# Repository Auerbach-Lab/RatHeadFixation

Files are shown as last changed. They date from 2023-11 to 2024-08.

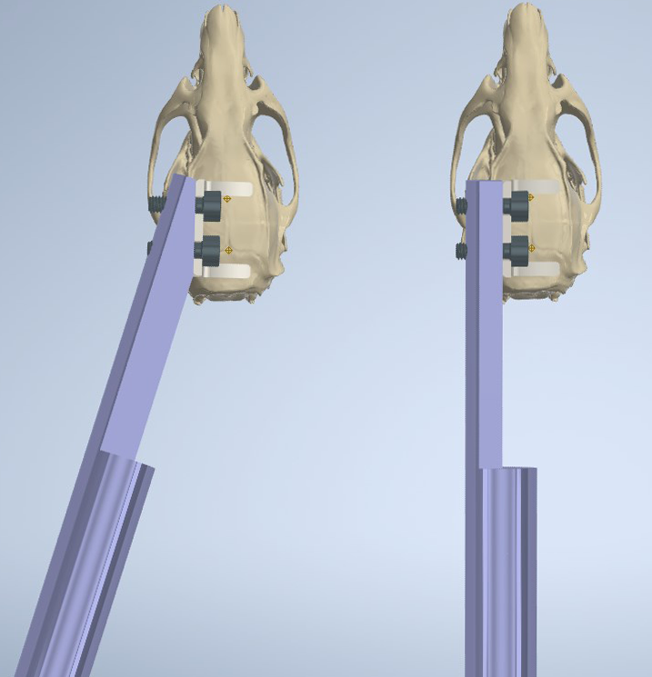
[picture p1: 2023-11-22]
Hight Adaptation/usage_headbars.png

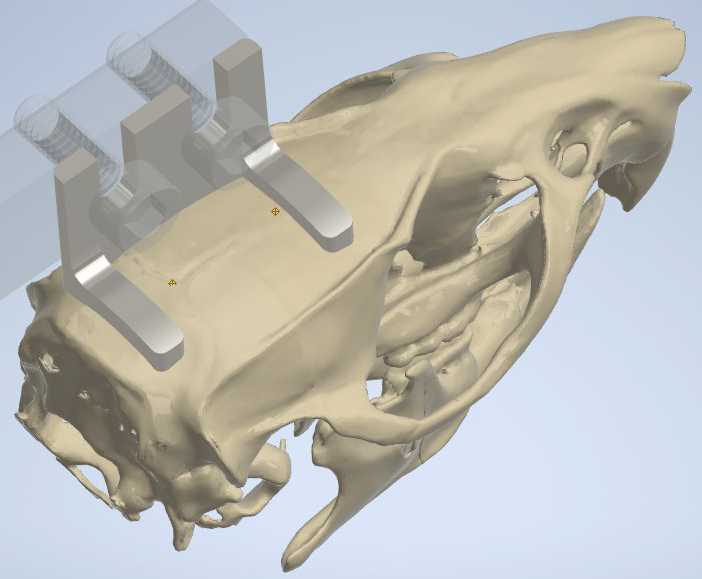
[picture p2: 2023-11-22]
Hight Adaptation/usage_ax_v03.png

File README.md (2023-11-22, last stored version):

# Rat Head Fixation System

 - **Author:** Brian James, \<james29@illinois.edu>
 - **Date:** 2022-08-20
 - **Version:** 0.3.5
 - **Primary Investigator:** Ben Auerbach, Auerbach Lab, University of Illinois \<bda5@illinois.edu>

## Description
This is a head fixation system for adult laboratory rats, suitable for audiology research. It is derived from the Hight mouse head fixation system. Headplates were re-created using the Hight plates as guidance, but in larger dimensions and contoured to match a CT scan of a rat skull. The mounting hole spacing was widened to minimize torque, and the mating portion of the angled headbar was thickened for additional strength. Because of the different mounting hole spacing, the two systems do not share interchangable parts.

## Parts
**rat_headplateACx** -- The primary headplate design, compatible with straight or angled headbar. This design is symmetrical; it can be used with the mounting plate on the left or the right side interchangably. Headplates can be 3d printed in stainless steel (such as 316) from a variety of manufacturers; [Craftcloud](craftcloud3d.com) allows easy comparison shopping. 

**rat_headplateIC** -- Alternative headplate suitable for probing the inferior colliculus or other regions requiring a dorsal approach. This design is compatible with straight headbar only. While it will mate with the angled headbar, the bar would need to pass downward through the bench top when securing a prone rat. This design is necessarily asymmetrical but can be mirrored for use with a right side headbar. This design is still version 0.1.

**rat_headbarStraight** -- Simple rod to which the plate is secured while in use, machined from 0.5" diameter rod stock, e.g. [Grainger #3ANN6](https://www.grainger.com/product/GRAINGER-APPROVED-Rod-Stock-316-3ANN6). Stainless steel alloy 316 is recommended for its improved resistance to corrosion, particularly if using cleaning solutions that decompose to produce chloride ions, such as bleach or benzalkonium chloride (Lysol, Microban, 3M Quat, most disinfecting wipes, etc).

**rat_headbarAngled** -- An alternative headbar design which may be useful if positioning the rat on a floating ball or similar movable surfaces.

**#5-40 Socket Head Cap Screw, 3/8 Length, 3/32 Hex"** -- Two screws are required per head**bar** for fastening a headplate, e.g. [Grainger #6XA50](https://www.grainger.com/product/GRAINGER-APPROVED-Socket-Head-Cap-Screw-5-40-6XA50).

**3/32 Hex Key / Allen Wrench** -- Socket head screws are driven using a hex key, e.g. [Grainger #38TG47](https://www.grainger.com/product/EKLIND-Hex-Key-3-32-in-Tip-Size-38TG47), rather than a screwdriver. A ball-end key is more convenient since it can be used at multiple angles. Verify the drive size of the fasteners you're using; #5 screws may require either 5/64" or 3/32" drive.

**C&B Metabond Dental Cement System** -- Only the following components are specifically
required:

 - Etchant Gel (S395)
 - Quick Base (S398)
 - C Universal TBB Catalyst (S371)
 - Radiopaque Tooth Shade Powder (S396)
 - Measuring Scoop (S378)
 - Ceramic Mixing Dish With Temperature Indicator (S387)

The remaining components from the all-in-one kit (S380) -- dentin activator, clear powder, applicator tools and brushes -- are not needed. If purchasing the kit, the clear powder may also be used interchangably with the opaque powder.

**Speedball India Ink** -- Used for dyeing the cement mixture. This brand is specifically
recommended by Hight for its consistency and imparted blackness.

**Toothpicks** and **Cotton/Foam Swabs** -- Used to apply cement and etchant, respectively.

## Files
The master assembly file is `rat_head_fixation_assembly.iam`, which shows how parts fit together and sit on the skull. That assembly and the individual `.ipt` part files are in Autodesk Inventor formats.

Dimensional drawings of the headbars are provided as `.dwg` Autodesk drawings and as PDFs, to be given to a machine shop. Only imperial unit versions are provided since both the base rod stock and the fasteners are in imperial units. Metric users should redefine the headbar to be machined from metric rod stock, probably 12 mm, and change the tapped holes to M3. No dimensional drawings are provided for headplate files, as these are intended to be 3d printed directly from the `.ipt` or `.stl` files. Part `.stl` files are dimensioned in millimeters.

Other provided files include the rat skull model in its original format (`RatSkull_Mesh1.stl`), a cropped version with a reduced vertex count created in Autodesk Meshmixer (`ratskull.mix`), and intermediate `.obj` files and corresponding `.ipt` files for the skull and cutaway profile views. There is also a sample 16x Nikon LWD microscope objective model to test clearance.

All files created for the Rat Head Fixation System have filenames prefixed with `rat` to differentiate them from similar Hight files. Manufacturer-provided files such as fasteners were not renamed.

## Usage
The AX headplate is intended to be positioned just forward of bregma, nearer to bregma
than to lambda, as pictured below. The angled headbar can be used when there needs to be
clearance behind the rat, such as when using a floating ball setup.

  

### Directions
1. Remove the ceramic mixing dish from freezer and place over ice to keep it cold.
2. Thoroughly clean cranium of any remaining tissue/periosteum and moisture.
3. Saturate swab with etchant, then apply swab over cleaned cranium surface. Let stand 30 seconds, then immediately and thoroughly wipe off with a clean swab. Be careful to not let etchant contact any soft tissue.
4. Position and fixate the headplate over the cranium using the headbar.
5. Prepare the cement. With the mixing dish still on ice, add (in this order) to one well: **4-5 drops Quick Base** (immediately re-cap container), **1 drop India Ink**, **1 drop Catalyst**  (immediately re-cap syringe). Mix gently, for no more than 5 seconds. Finally, add **2 scoops Radiopaque Powder** and stir gently for 5-10 seconds to a creamy consistency.
6. Using clean toothpicks, apply cement mixture to bond the cranium and headplate. Once applied to the headplate, the cement quickly solidifies in seconds to minutes.
7. Clean ceramic mixing dish before cement fully cures.
8. Allow the cement to set for 6 minutes (and allow at least 30 minutes before applying force to the headplate). Afterward, leave no part of the cranium exposed to air.

### Notes
 - Store the ceramic mixing dish in the freezer to ensure it is thoroughly chilled before use.
 - For best results, store mixing dish upside down, with water added to fill the base so that the entire dish is in contact with ice for the procedure.
 - Cured cement on instruments or the mixing dish can be softened by soaking in acetone or chloroform.
 - Coating surfaces in KY, petroleum jelly, glycerine, or mineral oil will prevent cement from bonding to them.
- Cement viscosity increases over time after being mixed.
- Working time for the cement mixture is 2 minutes at 15°C, or up to 5 minutes if kept colder. If the mixture is allowed to come to room temperature (24°C) the working time is cut to 20 seconds or less.
- Headplate implantations using this technique have been tested to be functional for at least 3 months.

## Sources
**Hight Mouse Head Fixation System**
Sandra Romero, Ariel E Hight, Kameron K Clayton, Jennifer Resnik, Ross S Williamson, Kenneth E Hancock, Daniel B Polley, Cellular and Widefield Imaging of Sound Frequency Organization in Primary and Higher Order Fields of the Mouse Auditory Cortex, _Cerebral Cortex_, Volume 30, Issue 3, March 2020, Pages 1603–1622, https://doi.org/10.1093/cercor/bhz190

**3D .stl File of Rat Skull**
M. Pohl, Bernd; Fernando Gasca; Olaf Christ; Hofmann, Ulrich G. (2013): 3D .stl file of rat skull. figshare. Dataset. https://doi.org/10.6084/m9.figshare.777745.v1

**3D .stl File of Mouse Skull**
Rowe T, Demarest M. (2001): "Mus musculus". Dataset: Digital Morphology. http://digimorph.org/specimens/Mus_musculus/

**Mouse Skull from Mouse skull (from micro-CT)**
https://www.thingiverse.com/thing:20200 by [MarkU](https://www.thingiverse.com/MarkU)


**16X Nikon CFI LWD Plan Fluorite Objective - CAD files**
https://www.thorlabs.com/thorproduct.cfm?partnumber=N16XLWD-PF

**Socket Head Cap Screw - CAD files**
https://www.grainger.com/product/GRAINGER-APPROVED-Socket-Head-Cap-Screw-5-40-6XA50

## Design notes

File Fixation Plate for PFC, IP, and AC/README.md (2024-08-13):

# Rat Head Fixation System

 - **Author:** Brian James, \<james29@illinois.edu>
 - **Date:** 2024-06-05
 - **Version:** 2.4
 - **Primary Investigator:** Ben Auerbach, Auerbach Lab, University of Illinois \<bda5@illinois.edu>

## Description
This is a novel head fixation system for adult laboratory rats, suitable for audiology research, intended to allow free access to the inferior colliculus, prefrontal cortex, and auditory cortex.

## Files
**Assembly - v4** -- The headplate and fixation aseembly. Headplates can be 3d printed in stainless steel (such as 316) from a variety of manufacturers; [Craftcloud](craftcloud3d.com) allows easy comparison shopping. The leading edge of the headplate sits roughly along the coronal suture when properly positioned on the skull.

## Associated Parts
**Drilling template** -- Cut-down headplate with substantially reduced thickness to facilitate marking locations of screw holes onto the skull. Print in same material (i.e. steel) at same scaling compensation as the main headplate to ensure identical spacing.

**Pigma Micron marker, #01 (0.25mm)** -- This permanent marker fits within the drilling template's holes, allowing precise marks on the skull of the locations for burr holes. The 01 (0.25mm felt tip) size offers the best fit and leaves the largest possible mark. The smaller 005 (**not** 05) and 003 size also fit. Sharpie Ultra-Fine markers do not quite fit. Cover the area to be marked with a thin layer of cyanoacrylate glue (CA, super, krazy, vetbond) to get a dry surface for marking; this procedure is also supposed to increase the bonding strength of MetaBond.

**Button-head torx screws, #0-80 thread, 3/16" long** -- Two bone screws are optionally used per headplate, e.g. [McMaster #90910A667](https://www.mcmaster.com/90910A667/). The headplates are to be tapped with #0-80 threads on the provided holes to mate with the screws. **It is not necessary to completely tighten the screws**; the protrusion beneath the headplate should be carefully judged. The screws are intended for additional security only, as the thickness of the skull only allows approximately 1.5 complete threads embedded in bone, and requires precision on drilled hole diameter on the order of 50 microns to avoid easily pulling free. **C&B MetaBond should be used as the primary affixative** of the headplate. 

**Torx-plus bit (size IP5) & driver** -- Socket head screws are driven using a torx+ bit, e.g. [McMaster #54305A18](https://www.mcmaster.com/54305A18/). A mini ratcheting 1/4" shank driver e.g. [McMaster #52815A22](https://www.mcmaster.com/52815A22/) is appropriate for these bits. Torx-plus was chosen for its superior torque application given the extremely small size of the screws, and for its ability to easily 'grab' a screw simply by mating.

**Spiral or burr drill bit, 1.2mm diameter** -- #0 (1.52mm) screws mate with a 75% thread hole of 1.19mm, used for soft metals (brass, aluminum) and plastics, or with a 50% thread hole of 1.32mm for hard metals (iron, steel). The smaller the burr hole, the more bite you will have, but the more resistance you will encounter setting the screw, since the bone is not tapped. Since only 1-2 threads will interface with the bone, however, the lab's existing 1.2mm burr bit should be fine.

**Standoffs, 1/4"-20 thread, various lengths** -- A variety lengths of [standoffs](https://www.mcmaster.com/products/male-female-threaded-hex-standoffs/male-female-threaded-hex-standoffs-6/thread-size~1-4-20/material~stainless-steel-2/material~18-8-stainless-steel/), all of which can mate with the ThorLabs table and each other. These provide the clamping surface used with either end of the headplate. Extra standoffs allow use in combination to assemble a clamping surface at any desired height above the bed of the table.

**Threaded inserts, #6-32 to 1/4"-20** -- 
Threaded inserts [McMaster #90247A008](https://www.mcmaster.com/90247A008) are installed in the shortest pair of standoffs. Consider adding the remaining pair of inserts to the single most appropriate length of standoff as well. The inserts allow mating with the cam clamps that top the standoffs in use. Installation of threaded inserts is permanent. 

**Clamping handle with threaded stud, #6-32 thread, 3/8" long**  -- These clamps, e.g. [McMaster #5720K25](https://www.mcmaster.com/5720K25/) are fastened to the top standoffs in use, with the aid of the threaded inserts. They should be threaded into the standoff so that the plate can be quickly inserted onto the exposed threaded stud, so sandwiched between the circular plastic piece above and the standoff's surface below. Operating a clamp can be done one-handed in approximately a single second. When engaged, clamps exert up to 1400 N of clamping force.

## Assembly
Partial assembly, showing interactions of pieces in use
Partial assembly, showing relationships of pieces in use: two stacked standoffs, cam clamp, bone screw, and headplate. Yellow crosshairs indicate probe locations for PFC, IC, and AC. **Note the position of the headplate relative to the corornal suture.** The headplate fits standoffs positioned exactly 2" apart; the hole spacing on the ThorLabs air table is 1", so there will be one empty hole between the two locations where standoffs are inserted.
<br><br><br>

Partial assembly, showing position of lab rat Above, with position of lab rat visualized. A shorter standoff (not pictured) may be used in the center position between the standoffs used for clamps, to support the animal's jaw and head.
<br><br><br>

Using 3/16" screws, up to 6 full threads (~1.9mm) will protrude beneath the headplate. Before mixing the metabond, the surgeon should thread the screws to the desired depth, then back the screws until they are flush with the headplate's lower surface while counting the revolutions made. During the surgery, retighten the screws by the same number of revolutions to drive them to the predetermined depth.

**It is not necessary to tighten the head of the screw to sit flush against the headplate.** Doing so only adds one additional threading to the ~7 threads already engaged within the body of the headplate.

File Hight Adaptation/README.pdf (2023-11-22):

# Rat Head Fixatition System

Author: Brian James
Date: 2022-08-20
Version: 0.3.5
Contact: Ben Auerbach, Auerbach Lab, University of Illinois <bda5@illinois.edu>

## Descriptition

This is a head fifixatition system for adult laboratory rats, suitable for audiology research. It is derived from the Hight mouse head fifixatition system. Headplates were re-created using the Hight plates as guidance, but in larger dimensions and contoured to match a CT scan of a rat skull. The mountiting hole spacing was widened to minimize torque, and the matiting portition of the angled headbar was thickened for addititional strength. Because of the difffferent mountiting hole spacing, the two systems do not share interchangable parts.

## Parts

rat_headplateACx – The primary headplate design, compatitible with straight or angled headbar. This design is symmetrical; it can be used with the mountiting plate on the leftft or the right side interchangably. Headplates can be 3d printed in stainless steel (such as 316) from a variety of manufacturers; Craftftcloud (https://stackedit.io/craftcloud3d.com) allows easy comparison shopping.

rat_headplateIC – Alternatitive headplate suitable for probing the inferior colliculus or other regions requiring a dorsal approach. This design is compatitible with straight headbar only. While it will mate with the angled headbar, the bar would need to pass downward through the bench top when securing a prone rat. This design is necessarily asymmetrical but can be mirrored for use with a right side headbar. This design is stitill version 0.1.

rat_headbarStraight – Simple rod to which the plate is secured while in use, machined from 0.5" diameter rod stock, e.g. Grainger #3ANN6. (https://www.grainger.com/product/GRAINGER-APPROVED-Rod-Stock-316-3ANN6) Stainless steel alloy 316 is recommended for its improved resistance to corrosion, partiticularly if using cleaning solutitions that decompose to produce chloride ions, such as bleach or benzalkonium chloride (Lysol, Microban, 3M Quat, most disinfectiting wipes, etc).

rat_headbarAngled – An alternatitive headbar design which may be useful if posititioning the rat on a flfloatiting ball or similar movable surfaces.

#5-40 Socket Head Cap Screw, 3/8 Length, 3/32 Hex" – Two screws are required per headbar for fastening a headplate, e.g. Grainger #6XA50. (https://www.grainger.com/product/GRAINGER-APPROVED-Socket-Head-Cap-Screw-5-40-6XA50)

3/32 Hex Key / Allen Wrench – Socket head screws are driven using a hex key, e.g. Grainger #38TG47, rather than a screwdriver. A ball-end key is more convenient since it can be used at (https://www.grainger.com/product/EKLIND-Hex-Key-3-32-in-Tip-Size-38TG47) multitiple angles. Verify the drive size of the fasteners you’re using; #5 screws may require either 5/64" or 3/32" drive.

C&B Metabond Dental Cement System – Only the following components are specififically required:

Etchant Gel (S395)
Quick Base (S398)
C Universal TBB Catalyst (S371) Radiopaque Tooth Shade Powder (S396)
Measuring Scoop (S378)
Ceramic Mixing Dish With Temperature Indicator (S387)

The remaining components from the all-in-one kit (S380) – dentitin actitivator, clear powder, applicator tools and brushes – are not needed. If purchasing the kit, the clear powder may also be used interchangably with the opaque powder.

Speedball India Ink – Used for dyeing the cement mixture. This brand is specififically recommended by Hight for its consistency and imparted blackness.

Toothpicks and Cotttton/Foam Swabs – Used to apply cement and etchant, respectitively.

## Files

The master assembly fifile is rat_head_fixation_assembly.iam , which shows how parts fifit together and sit on the skull. That assembly and the individual .ipt part fifiles are in Autodesk

Inventor formats.

Dimensional drawings of the headbars are provided as .dwg Autodesk drawings and as PDFs,

to be given to a machine shop. Only imperial unit versions are provided since both the base rod stock and the fasteners are in imperial units. Metric users should redefifine the headbar to be machined from metric rod stock, probably 12 mm, and change the tapped holes to M3. No dimensional drawings are provided for headplate fifiles, as these are intended to be 3d printed directly from the .ipt or .stl fifiles. Part .stl fifiles are dimensioned in millimeters.

Other provided fifiles include the rat skull model in its original format ( RatSkull_Mesh1.stl ), a cropped version with a reduced vertex count created in Autodesk Meshmixer ( ratskull.mix ), and intermediate .obj fifiles and corresponding .ipt fifiles for the skull and cutaway profifile

views. There is also a sample 16x Nikon LWD microscope objectitive model to test clearance.

All fifiles created for the Rat Head Fixatition System have fifilenames prefifixed with rat to difffferentitiate them from similar Hight fifiles. Manufacturer-provided fifiles such as fasteners were not renamed.

## Usage

The AX headplate is intended to be posititioned just forward of bregma, nearer to bregma than to lambda, as pictured below. The angled headbar can be used when there needs to be clearance behind the rat, such as when using a flfloatiting ball setup.

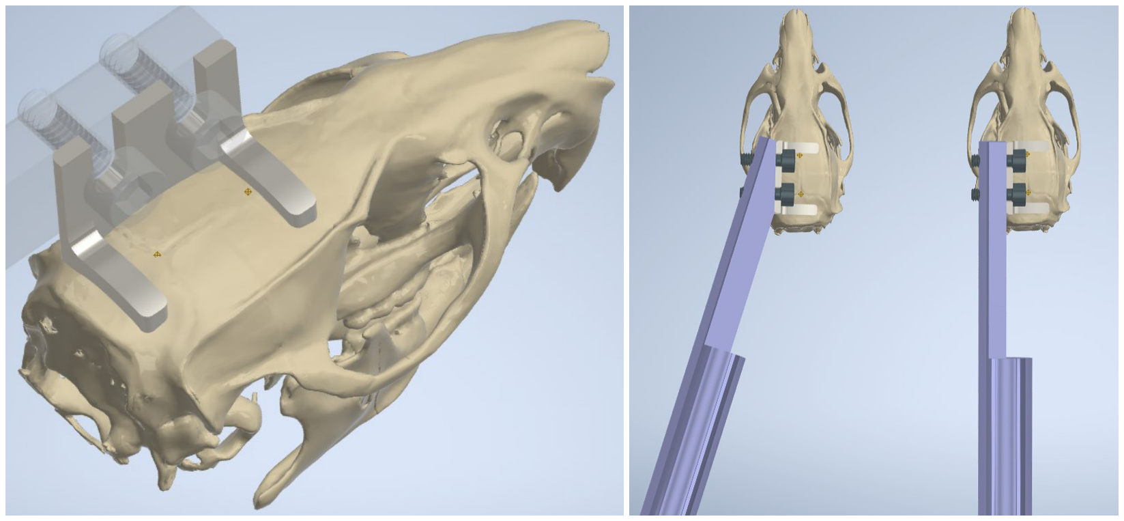
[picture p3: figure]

Directitions

1. Remove the ceramic mixing dish from freezer and place over ice to keep it cold.
2. Thoroughly clean cranium of any remaining titissue/periosteum and moisture.
3. Saturate swab with etchant, then apply swab over cleaned cranium surface. Let stand 30 seconds, then immediately and thoroughly wipe offff with a clean swab. Be careful to not let etchant contact any softft titissue.
4. Positition and fifixate the headplate over the cranium using the headbar.
5. Prepare the cement. With the mixing dish stitill on ice, add (in this order) to one well: 4-5 drops Quick Base (immediately re-cap container), 1 drop India Ink, 1 drop Catalyst (immediately re-cap syringe). Mix gently, for no more than 5 seconds. Finally, add 2 scoops Radiopaque Powder and stitir gently for 5-10 seconds to a creamy consistency.
6. Using clean toothpicks, apply cement mixture to bond the cranium and headplate. Once applied to the headplate, the cement quickly solidififies in seconds to minutes.
7. Clean ceramic mixing dish before cement fully cures.
8. Allow the cement to set for 6 minutes (and allow at least 30 minutes before applying force to the headplate). Aftfterward, leave no part of the cranium exposed to air.

Notes

Store the ceramic mixing dish in the freezer to ensure it is thoroughly chilled before use. For best results, store mixing dish upside down, with water added to fifill the base so that the entitire dish is in contact with ice for the procedure.
Cured cement on instruments or the mixing dish can be softftened by soaking in acetone or chloroform.
Coatiting surfaces in KY, petroleum jelly, glycerine, or mineral oil will prevent cement from bonding to them.
Cement viscosity increases over titime aftfter being mixed.
Working titime for the cement mixture is 2 minutes at 15°C, or up to 5 minutes if kept colder. If the mixture is allowed to come to room temperature (24°C) the working titime is cut to 20 seconds or less.
Headplate implantatitions using this technique have been tested to be functitional for at least 3 months.

## Sources

Hight Mouse Head Fixatition System
Sandra Romero, Ariel E Hight, Kameron K Clayton, Jennifer Resnik, Ross S Williamson, Kenneth E Hancock, Daniel B Polley, Cellular and Widefifield Imaging of Sound Frequency Organizatition in Primary and Higher Order Fields of the Mouse Auditory Cortex, Cerebral Cortex, Volume 30, Issue 3, March 2020, Pages 1603–1622, httttps://doi.org/10.1093/cercor/bhz190

Mouse Skull from Mouse skull (from micro-CT) httttps://www.thingiverse.com/thing:20200 by MarkU (https://www.thingiverse.com/MarkU)

3D .stl File of Rat Skull
M. Pohl, Bernd; Fernando Gasca; Olaf Christ; Hofmann, Ulrich G. (2013): 3D .stl fifile of rat skull. fifigshare. Dataset. httttps://doi.org/10.6084/m9.fifigshare.777745.v1 (https://doi.org/10.6084/m9.figshare.777745.v1)

16X Nikon CFI LWD Plan Fluorite Objectitive - CAD fifiles httttps://www.thorlabs.com/thorproduct.cfm?partnumber=N16XLWD-PF

Socket Head Cap Screw - CAD fifiles httttps://www.grainger.com/product/GRAINGER-APPROVED-Socket-Head-Cap-Screw-5-40-6XA50 (https://www.grainger.com/product/GRAINGER-APPROVED-Socket-Head-Cap-Screw-5-40-6XA50)

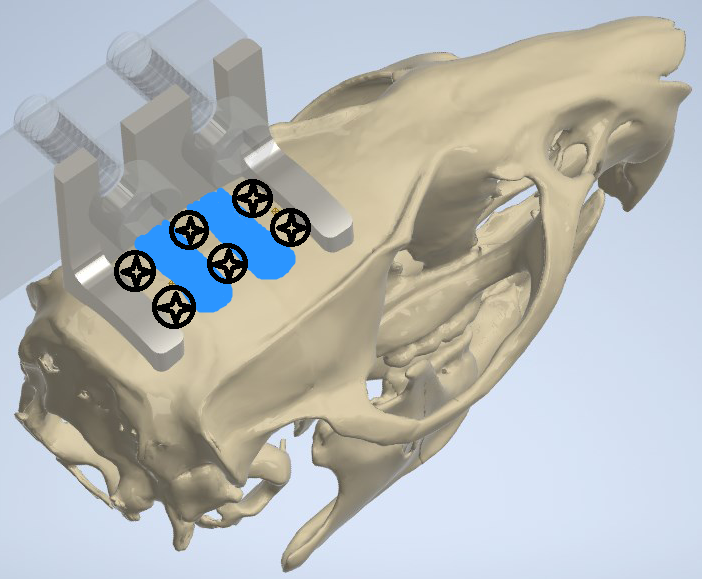
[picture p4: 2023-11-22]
Hight Adaptation/modification3.png

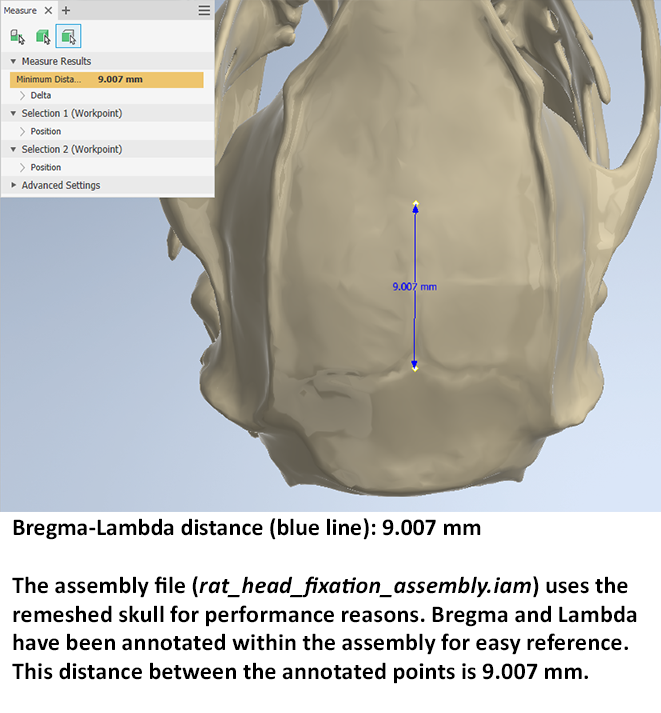
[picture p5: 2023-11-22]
Hight Adaptation/B-L distance (iam).png

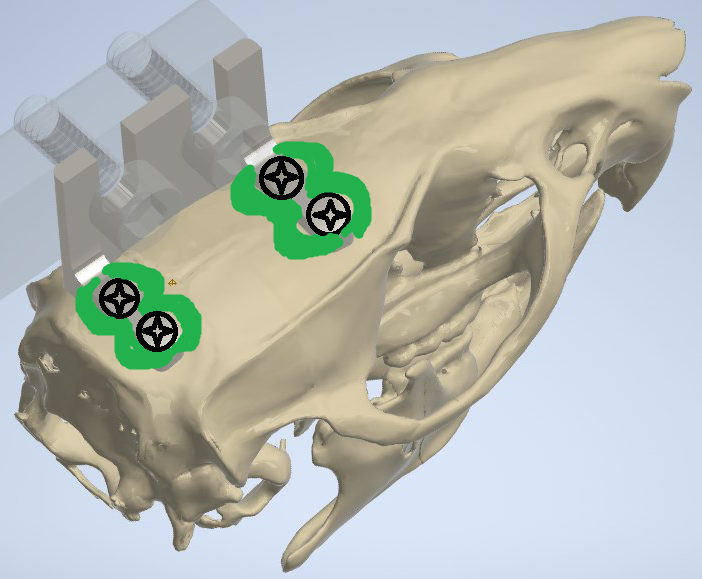
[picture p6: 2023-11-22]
Hight Adaptation/modification4.png

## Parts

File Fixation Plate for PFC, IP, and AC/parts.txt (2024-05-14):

part									description					qty
https://www.mcmaster.com/91075A198		1.5" lg 1/4-20 standoff		4
https://www.mcmaster.com/91075A196		1.0" lg 1/4-20 standoff		2
https://www.mcmaster.com/91075A258		3/4" lg 1/4-20 standoff		2
https://www.mcmaster.com/91075A192		0.5" lg 1/4-20 standoff		2
https://www.mcmaster.com/91197A420   	0.5" lg 1/4-20 standoff		2
https://www.mcmaster.com/91197A430		5/8" lg 1/4-20 standoff		2
https://www.mcmaster.com/91197A440/		3/4" lg 1/4-20 standoff		2

https://www.mcmaster.com/5720K25		6-32 cam clamp 3/8" lg		2
https://www.mcmaster.com/90247A008		6-32 to 1/4-20 inserts		1 (pkg of 5)

For 00-96 holes:
https://www.mcmaster.com/90910A440		00-96 screws, torx+, 1/8"	1 (pkg of 100)
https://www.mcmaster.com/54305A42		IP2 torx+ bit				2
https://www.mcmaster.com/52815A22		ratcheting driver			1

For 00-90 holes:
https://www.mcmaster.com/96710A050/		00-90 screws, torx+, 1/8"	4 (pkg of 25)
https://www.mcmaster.com/54305A42		IP2 torx+ bit				2
https://www.mcmaster.com/52815A22		ratcheting driver			1

For 0-80 holes:
https://www.mcmaster.com/90910A665/		0-80 screws, torx+, 1/8"	4 (pkg of 25)
https://www.mcmaster.com/54305A18/		IP5 torx+ bit				2
https://www.mcmaster.com/52815A22		ratcheting driver			1

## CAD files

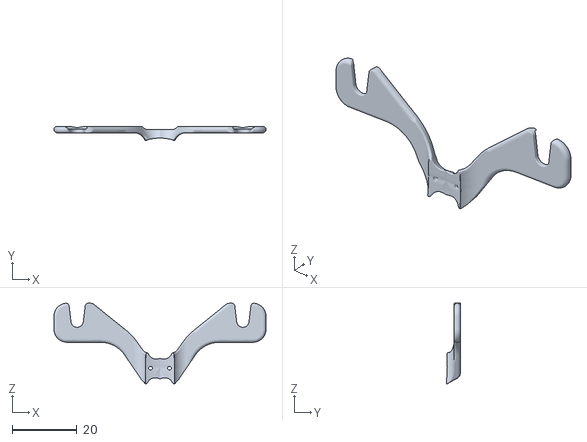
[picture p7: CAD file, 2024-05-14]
Fixation Plate for PFC, IP, and AC/interface v4 101%.stl
65.7 x 4.46 x 25.0

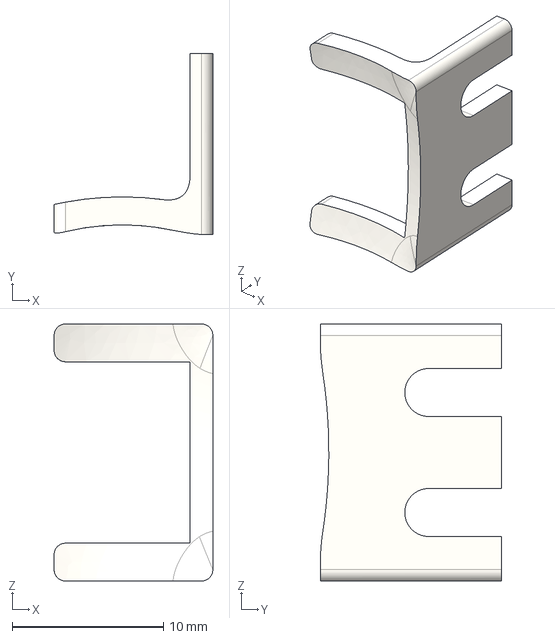
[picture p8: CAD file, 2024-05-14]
Hight Adaptation/rat_headplateACx.stp
10.5 x 12.0 x 17.0 mm

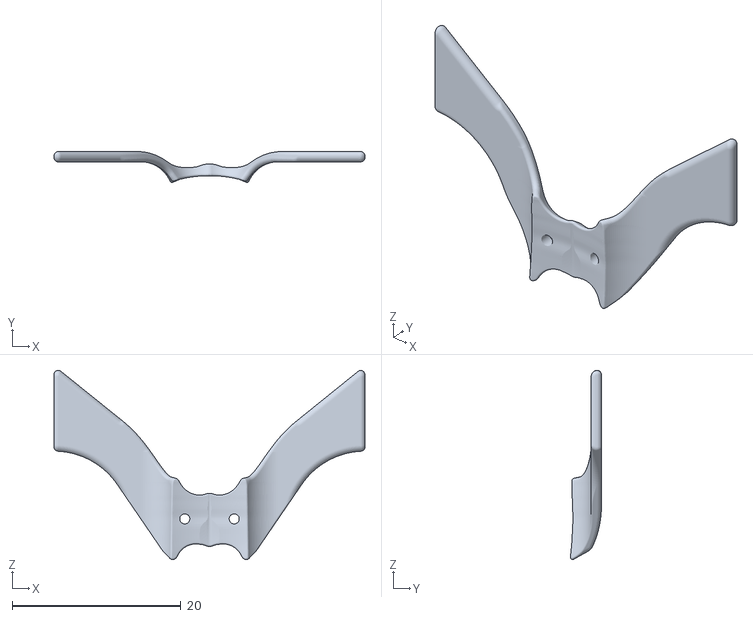
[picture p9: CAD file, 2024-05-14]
Fixation Plate for PFC, IP, and AC/drilling template 101%.stl
36.9 x 3.67 x 22.4

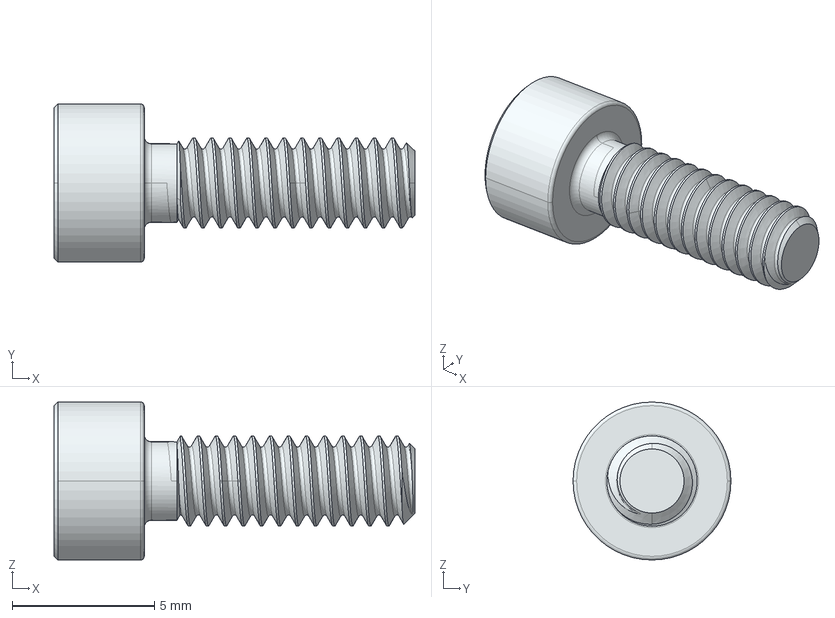
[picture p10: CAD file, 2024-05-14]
Hight Adaptation/grainger-26kv60.stp
12.7 x 5.56 x 5.56 mm

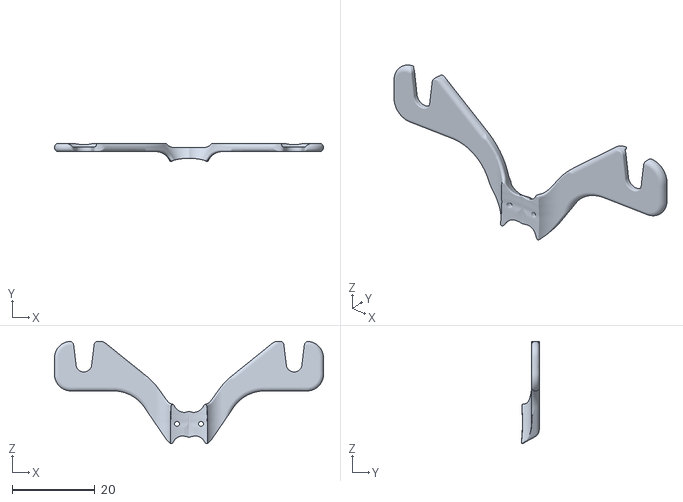
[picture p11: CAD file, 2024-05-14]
Fixation Plate for PFC, IP, and AC/interface - v4.stl
65.0 x 4.42 x 24.7

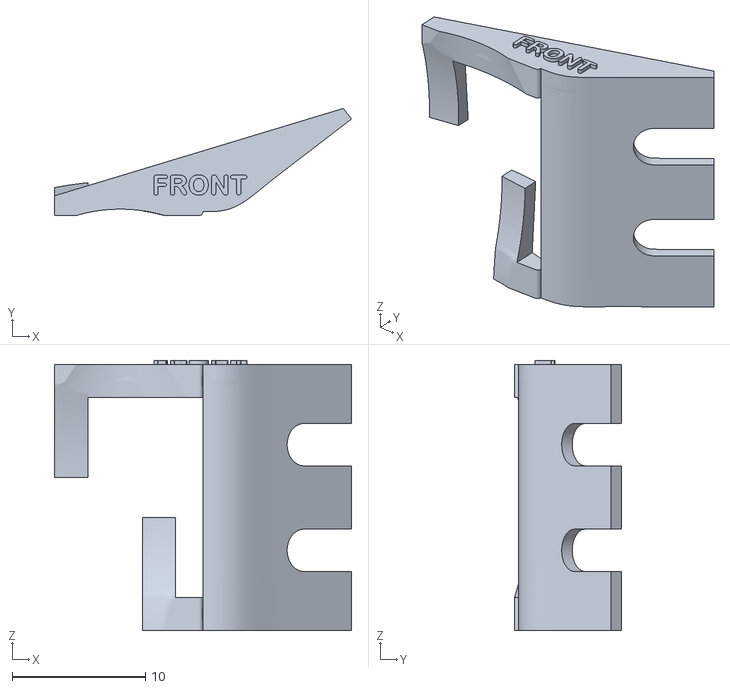
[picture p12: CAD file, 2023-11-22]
Hight Adaptation/rat_headplateIC.stl
22.3 x 8.05 x 20.3

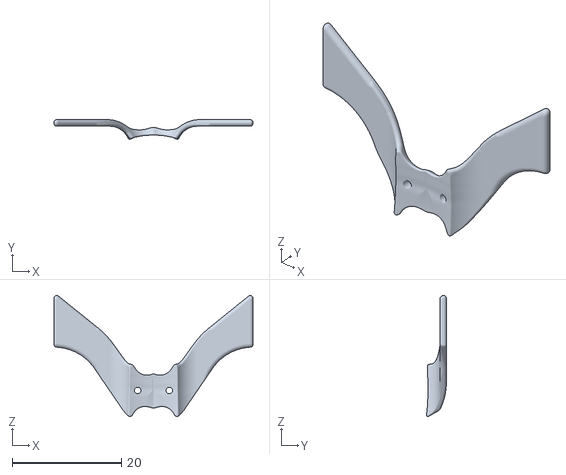
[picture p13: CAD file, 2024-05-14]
Fixation Plate for PFC, IP, and AC/drilling template.stl
36.5 x 3.64 x 22.2

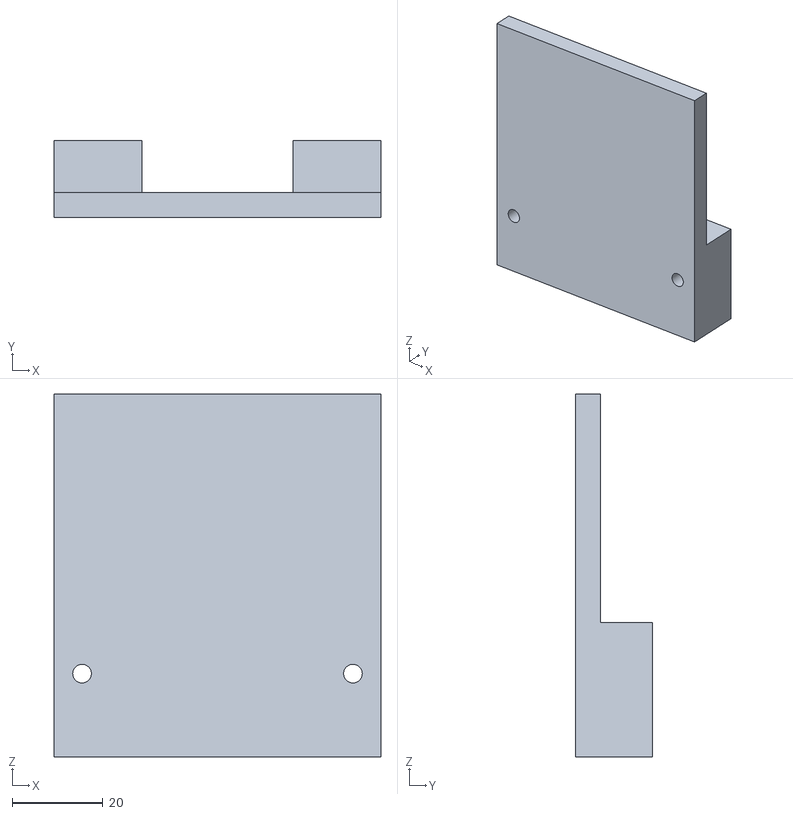
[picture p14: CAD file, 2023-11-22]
Hight Adaptation/Headplate holder base.STL
72.0 x 17.0 x 80.0

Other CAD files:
Hight Adaptation/rat_headbarStraight.dwg
Hight Adaptation/rat_headbarAngled.dwg
Fixation Plate for PFC, IP, and AC/0.5in_31325A27_Slip-Fit Tooling Ball with Threaded Hole.ipt
Fixation Plate for PFC, IP, and AC/5720K27_Clamping Handle with Threaded Stud.ipt
Fixation Plate for PFC, IP, and AC/91197A480_316 Stainless Steel Male-Female Threaded Hex Standoff.ipt
Fixation Plate for PFC, IP, and AC/Assembly - v4.iam
Fixation Plate for PFC, IP, and AC/B3048F-thorlabs-airtable-breadboard.ipt
Fixation Plate for PFC, IP, and AC/drilling template.iam
Fixation Plate for PFC, IP, and AC/interface - v4.ipt
Fixation Plate for PFC, IP, and AC/labrat92.ipt
Fixation Plate for PFC, IP, and AC/skull-95w.ipt
Fixation Plate for PFC, IP, and AC/z32.ipt
Fixation Plate for PFC, IP, and AC/z64.ipt
Fixation Plate for PFC, IP, and AC/zd64.ipt
Hight Adaptation/001_MACHINE_SCREW_ST_PRT_AF6.ipt
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

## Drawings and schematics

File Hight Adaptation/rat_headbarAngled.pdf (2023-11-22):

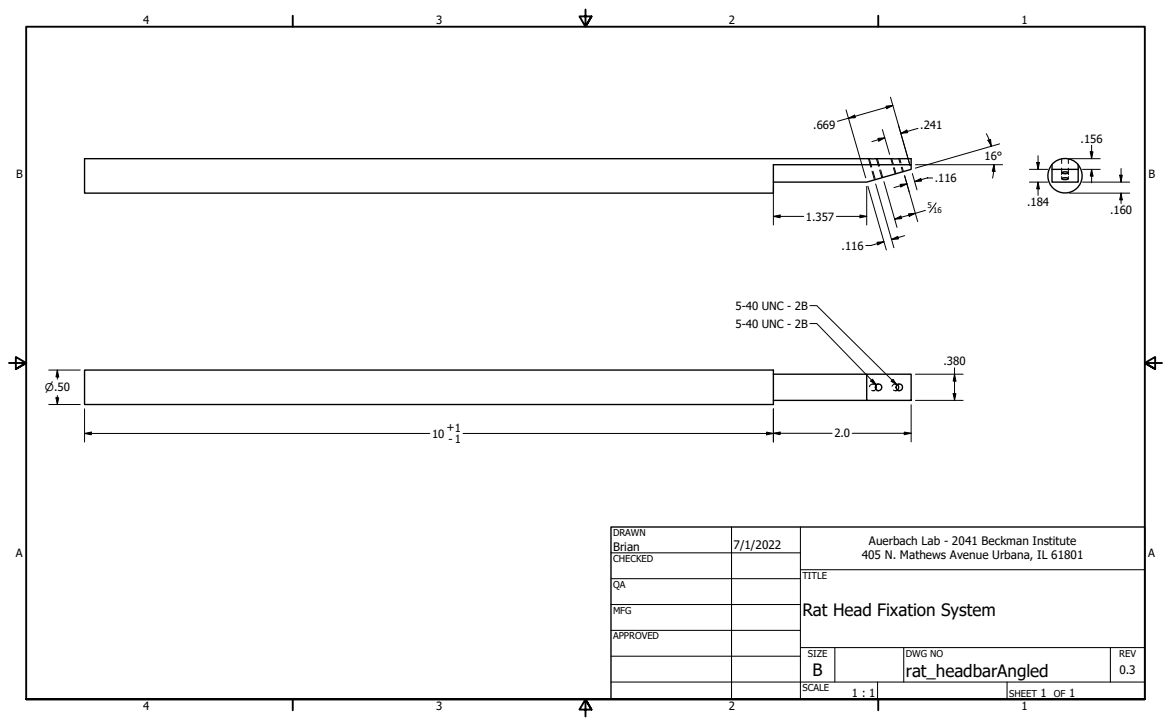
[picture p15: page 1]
5-40 UNC - 2B

DRAWN Brian | 7/1/2022 | Auerbach Lab - 2041 Beckman Institute 405 N. Mathews Avenue Urbana, IL 61801

CHECKED

MFG

Rat Head Fixation System

APPROVED

SIZE B | DWG NO rat_headbarAngled | REV 0.3

SCALE 1 : 1 | | SHEET 1 OF 1

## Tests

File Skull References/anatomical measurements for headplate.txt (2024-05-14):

New		Rat_skull+mandible_high_res, the file with clear sutures
Old		RatSkull_Mesh1 and derivatives, ratskull.ipt, the file with vertebrae
Nor		RatSkullSTL, Rattus norvegicus, the file that is just a smoothed cranium alongside a lower jaw file
iRR		Indonesian Rattus Rattus skull, physical, from ebay, probably actually R. norvegicus by dimensions
mRN		"Morphometric" paper, Rattus norvegicus
mRR		"Morphometric" paper, Rattus rattus
2022	the claims in the table below this one
Lab		Manasi's measurements average
Min		Manasi's minimums

location letters come from Figure 4 of "Morphometric Study of Mus musculus, Rattus norvegicus, and Rattus rattus in Qatar"

																							  yup, was
																							  too big!
														2022	iRR		Lab		Min		New		Old		Nor		mRN		mRR
maximal frontal bone parietal sutures (PQ), interior	12.1	 9.8	9.7		9.1		10.2	12.2	 9.6		
maximal frontal bone parietal sutures (PQ), exterior			12.1					11.6	13.7	11.9	10.9	10.3
parietal distance through bregma, interior				13.1	10.9					11.5	13.6	10.4	
bregma-lambda distance sutures not true/idealized (DE)   		 8.7	7.8		6.2		 7.8	8.4		 7.6
interparietal bone width (TU), interior							 9.8	10.4	9.3		11.1	13.4	10.5
interparietal bone width (TU), exterior					~16		14.5					12.9	16.2	12.7	11.5	10.7
frontal bone length (CD)										16.2	14.4	12.3	13.8	15.8	16.6	14.7	12.2
narrowest intraorbital breadth (LM), exterior			5.6		 6.0					 6.1	 6.6	 5.8	 6.8	5.8

Manasi's measurements 									♀1		♀2		♀3		♀4		♂1		♂2		♂3		♂4		♂5		Avg
maximal frontal bone parietal sutures (PQ), interior	9.9		9.8		10.0	9.5		10.5	9.1		9.5		9.6		9.0		9.7
bregma-lambda distance sutures not true/idealized (DE)	7.3		6.7		6.7		6.2		8.8		8.5		9.9		7.6		8.3		7.8
interparietal bone width (TU), interior					11.0	11.0	11.3	10.0	10.3	10.0	9.3		11.1	9.5		10.4
frontal bone length (CD)								14.2	13.0	13.1	12.3	14.4	15.2	16.0	15.9	15.4	14.4	

so			new=Rat_skull+mandible_high_res, the file with clear sutures (as above)
			for ALL files, the cranium was rotated -0.75 degrees about the z axis
atlas		new scaled to 107% to match to correspond closely to stereotaxic atlas 
unscaled	new's dimensions baseline
95w			new's width (transverse dimension) squished to 95% ie 9.7/10.2, the PQ distance.
min			new squashed to 83% width ie 9.3/11.1 (TU), 79% length ie 6.2/7.8 (DE), and height set to 81 for consistency of skull shape
ATLMIN		atlas squashed uniformly to 75% (80% of new) so that TU~9.3, DE~6.2		(not yet created)
ATLMED		atlas squashed uniformly to 89% (95% of new) so that PQ~9.7				(not yet created)

2022 claims - take with grain of salt since we didn't have as much room as expected
														mouse	rat
narrowest facial bone distance							3.4		5.6
frontal distance, at zygoma midpoint					4.4		9.4
frontal distance, above mandibular coronoid process		5.6		12.6
parietal distance, through bregma						9.1		13.1
parietal distance, through lambda, inside crests		6.9?	12.1
narrowest interparietal span							5.4		9.9
superior cranial width									9.9		14.0
peak height over supraorbital ridge						1.9		2.1
fore brace is between zygoma midpoint and bregma
rear brace is just behind lambda
anterior  face of fore brace, intra-arch distance		3.65	~ narrowest facial
posterior face of fore brace, intra-arch distance		4.95	< coronoid width
anterior  face of rear brace, intra-arch distance		6.05	< lambda width
posterior face of rear brace, intra-arch distance		5.37	= narrowest interparietal

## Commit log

2023-11-22 Initial upload
    [001_MACHINE_SCREW_ST_PRT_AF6.ipt, Headplate holder base.STL, N16XLWD-PF.ipt, grainger-26kv60.stp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]
2024-05-14 Move 2022 work to dedicated directory
    [001_MACHINE_SCREW_ST_PRT_AF6.ipt, Headplate holder base.STL, N16XLWD-PF.ipt, grainger-26kv60.stp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]
2024-05-14 Add 2024 work and skull references
    [0.5in_31325A27_Slip-Fit Tooling Ball with Threaded Hole.ipt, 001_MACHINE_SCREW_ST_PRT_AF6.ipt, 5720K27_Clamping Handle with Threaded Stud.ipt, 91197A480_316 St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]
2024-05-14 Add larger skull reference IPTs in LFS
    [skull-95w (original with history).ipt, skull-min.ipt]

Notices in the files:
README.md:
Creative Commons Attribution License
